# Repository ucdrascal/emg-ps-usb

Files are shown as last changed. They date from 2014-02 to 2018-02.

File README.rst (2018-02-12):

==========
emg-ps-usb
==========

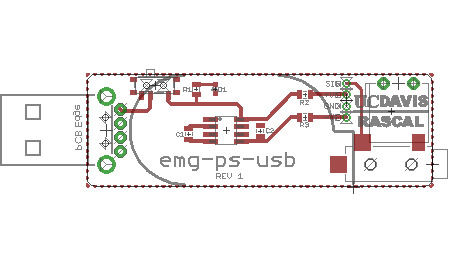
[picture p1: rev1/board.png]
Board screenshot


Description
===========
This is a power supply design for powering Motion Lab Systems Y03 or Z03 EMG
preamplifiers with a standard USB port. The board is designed to function like
a USB dongle with EMG electrode leads coming from it and a 1/8" `TS phone
connector`_ output (e.g. to connect to a computer's microphone port).

It uses a charge pump voltage converter chip to generate -5V from +5V USB
power. It is recommended that the design in the current state be used only with
USB ports belonging to devices isolated from mains earth (ground). This is
because there is no galvanic isolation between the USB port's ground and the
ground electrode, which connects directly to the user. It was originally
designed to connect to Android tablets which have a full-size USB A jack and
a TRRS headset inputs.

Parts
=====
Integrated circuits:

* `Analog Devices ADM660`_ switched-capacitor voltage converter

Electromechanical:

* Apem MA12R/TR SPDT switch
* CUI MJ-3523-SMT 3.5mmm mono phono jack
* Molex 480390001 USB-A connector
* TE Connectivity 284093-2 2x1 screw terminal block
* MyCableMart.com 6" 3.5mm mono male to male cable

Discrete components:

* Samsung CL21A106KAYNNNE 10uF ceramic capcaitor
* Panasonic ERJ-6GEYJ101V 100 Ohm thick film resistor
* Panasonic ERJ-6GEYJ102V 1k Ohm thick film resistor
* OSRAM LS L29K-G1J2-1-Z red LED

Details, including vendor links and prices are in bill-of-materials.ods.

License
=======

The contents of this repository are licensed under the `CC-BY 4.0 license`_.

.. REFERENCES
.. _`Analog Devices ADM660`: http://www.analog.com/en/power-management/switched-capacitor-converters/adm660/products/product.html
.. _`TS phone connector`: https://en.wikipedia.org/wiki/Phone_connector_(audio)
.. _`CC-BY 4.0 license`: https://creativecommons.org/licenses/by/4.0/

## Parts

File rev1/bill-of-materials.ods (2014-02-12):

Manufacturer | Part Number | Description | Qty | Unit Price | Vendor Part Number | Vendor Link
Analog Devices | ADM660ARZ | Charge pump converter | 1 | 4.59 | ADM660ARZ-ND | http://www.digikey.com/product-detail/en/ADM660ARZ/ADM660ARZ-ND/820185
Molex Inc. | 480390001 | USB-A connector | 1 | 1.19 | WM17117-ND | http://www.digikey.com/product-detail/en/0480370001/WM17117-ND/857603
Apem Inc. | MA12R/TR | SPDT switch | 1 | 1.10 | 679-1847-1-ND | http://www.digikey.com/product-detail/en/MA12RTR/679-1847-1-ND/1973774
TE Connectivity | 284093-2 | 2x1 screw terminal block | 1 | 1.11 | A98369-ND | http://www.digikey.com/product-detail/en/284093-2/A98369-ND/1136747
CUI Inc. | MJ-3523-SMT | 3.5mm mono phone jack | 1 | 1.34 | CP-3523MJCT-ND | http://www.digikey.com/product-detail/en/MJ-3523-SMT/CP-3523MJCT-ND/669691
OSRAM Opto Semiconductors Inc | LS L29K-G1J2-1-Z | red LED | 1 | 0.17 | 475-2506-1-ND | http://www.digikey.com/product-detail/en/LS%20L29K-G1J2-1-Z/475-2506-1-ND/1802633
Panasonic Electronic Components | ERJ-6GEYJ102V | 1k Ohm resistor | 1 | 0.10 | P1.0KACT-ND | http://www.digikey.com/product-detail/en/ERJ-6GEYJ102V/P1.0KACT-ND/42833
Panasonic Electronic Components | ERJ-6GEYJ101V | 100 Ohm resistor | 2 | 0.10 | P100ACT-ND | http://www.digikey.com/product-detail/en/ERJ-6GEYJ101V/P100ACT-ND/21875
Samsung Electro-Mechanics America, Inc | CL21A106KAYNNNE | 10uF ceramic capacitor | 2 | 0.25 | 1276-2891-1-ND | http://www.digikey.com/product-detail/en/CL21A106KAYNNNE/1276-2891-1-ND/3890977
MyCableMart.com | FS-MONO-06IN-MM | 3.5mm mono male to male cable | 1 | 0.81 | FS-MONO-06IN-MM | http://www.mycablemart.com/store/cart.php?m=product_detail&p=4270
 |  |  | Subtotal | 11.11
 |  |  | Printing | 2.87
 |  |  | Total | 13.96

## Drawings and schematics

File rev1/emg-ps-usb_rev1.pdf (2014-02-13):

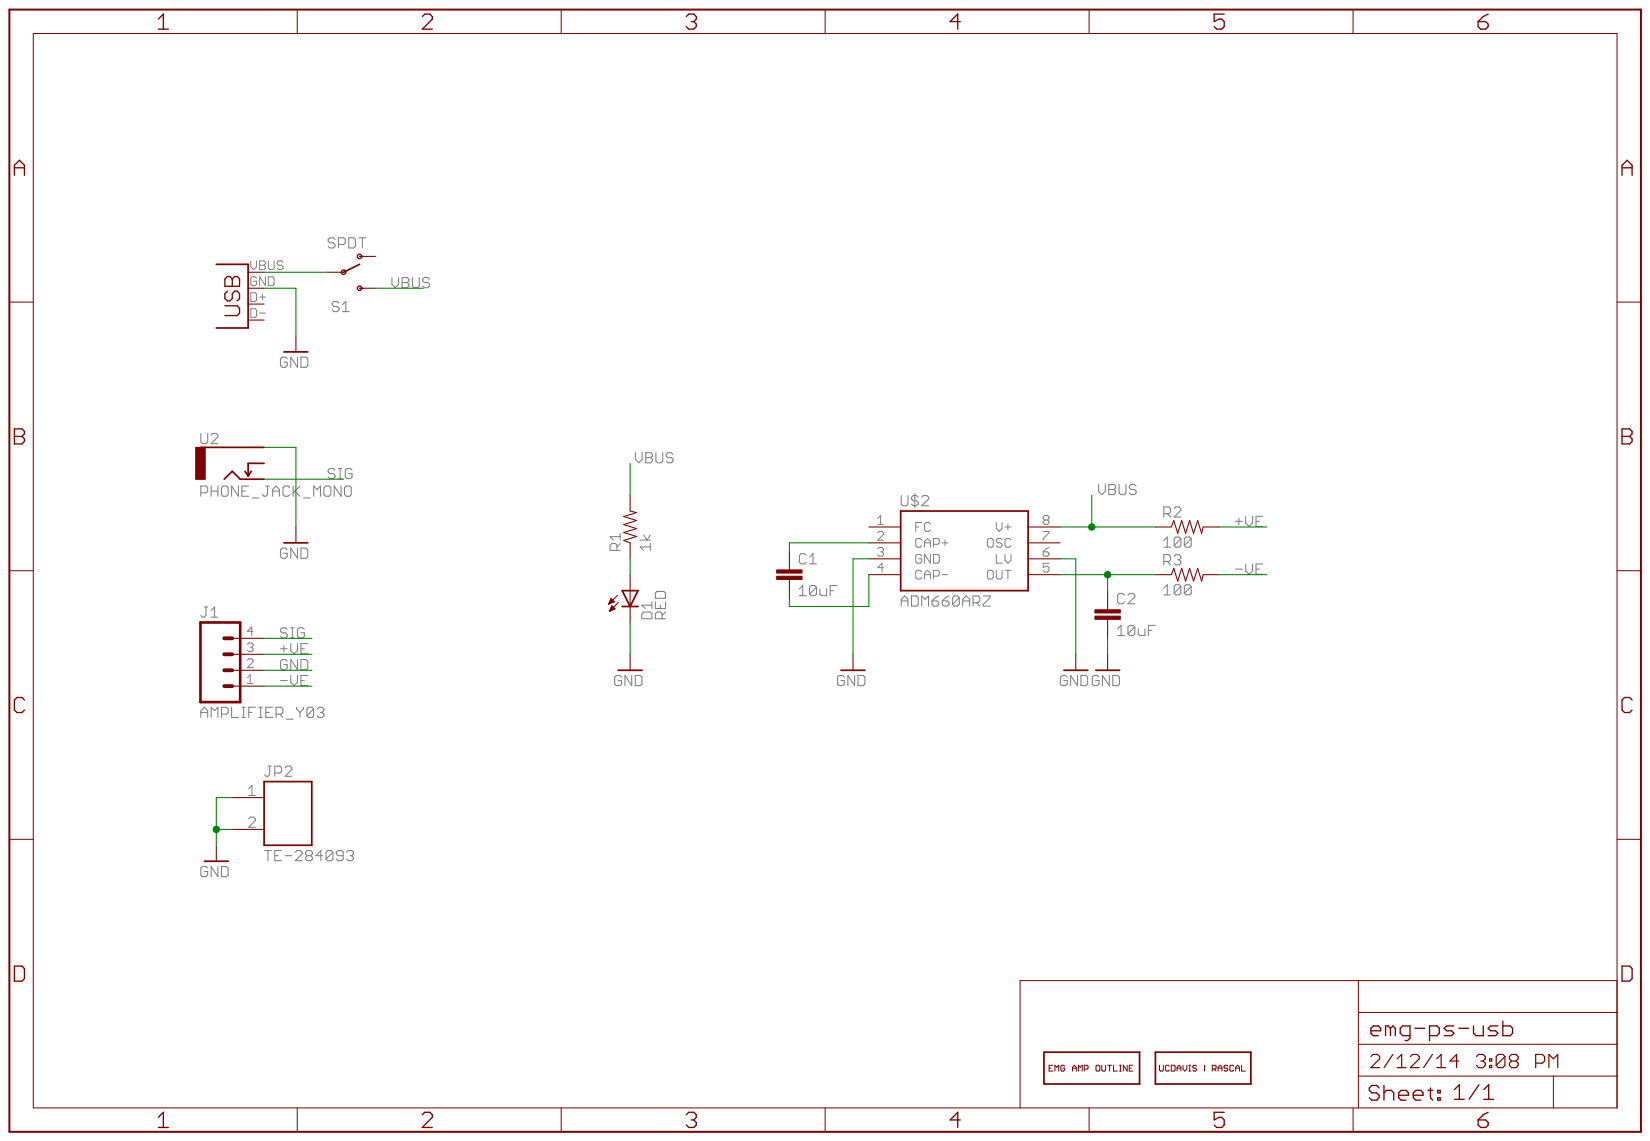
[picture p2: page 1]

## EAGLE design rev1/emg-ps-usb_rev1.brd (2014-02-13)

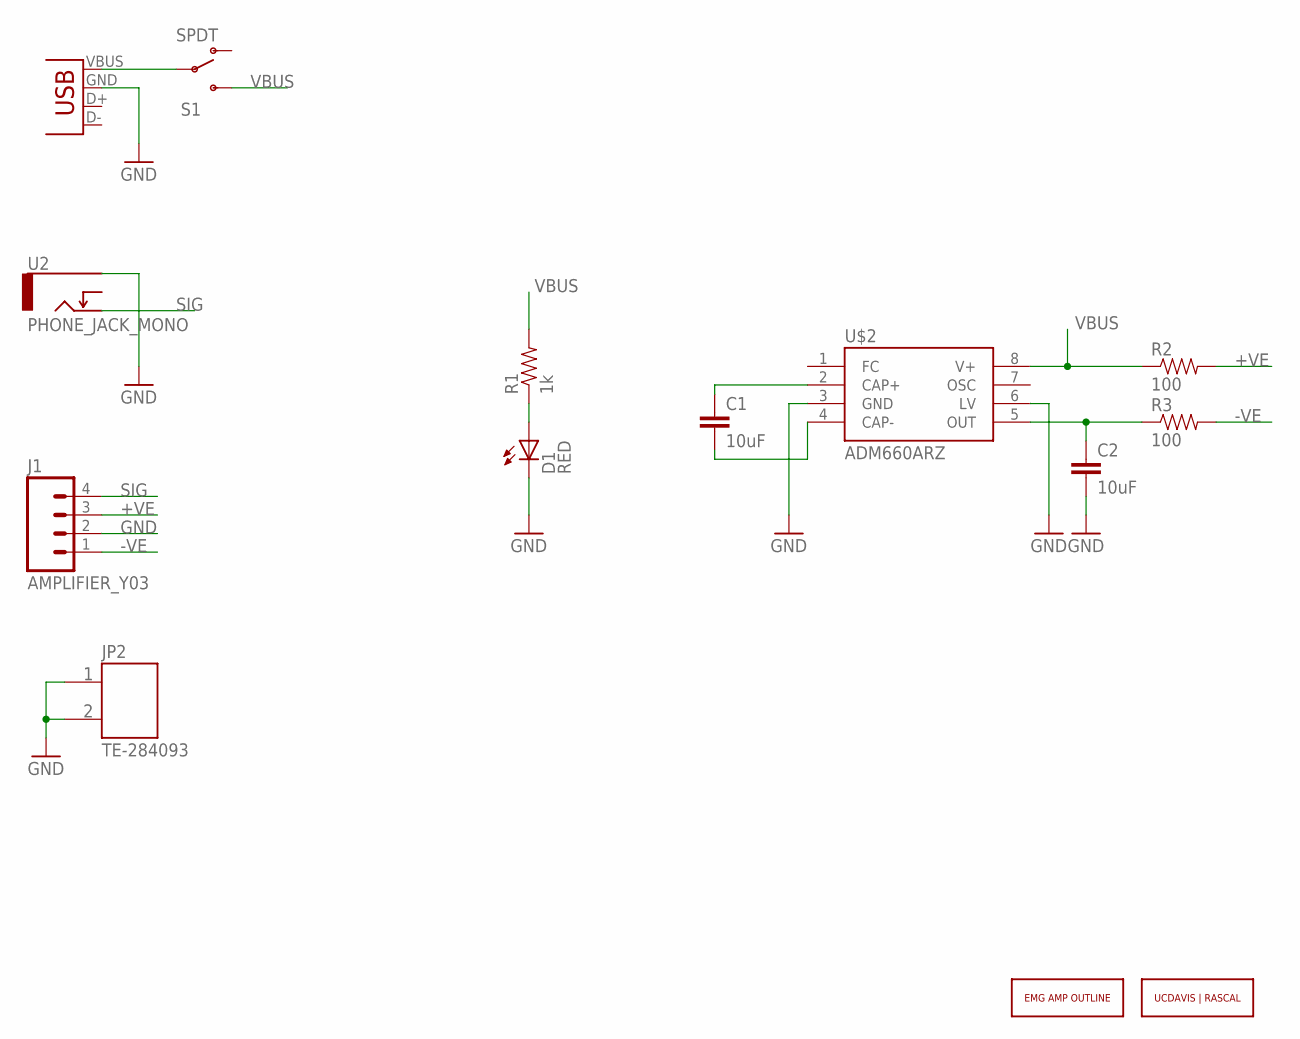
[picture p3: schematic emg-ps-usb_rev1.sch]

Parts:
C1, C2: 10uF; 0805
D1: RED; LED-0603
J1: AMPLIFIER_Y03; AMPLIFIER_WTB
JP1: USB-A-H
JP2: TE-284093
R1: 1k; 0805
R2, R3: 100; 0805
S1: SPDT; SWITCH-SPST-SMD-A
U2: PHONE_JACK_MONO; MJ-3523-SMT
U$1: UCDAVIS-RASCAL_LOGO-2LINE; UCDAVIS-RASCAL_LOGO
U$2: ADM660ARZ; SOIC8
U$3: EMG_AMP_OUTLINE-Y03ENDS; EMG_Y03_OUTLINEENDS

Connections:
+VE: J1.3, R2.2
-VE: J1.1, R3.2
GND: C2.2, D1.C, J1.2, JP1.GND (VBUS), JP2.P$1 (1), JP2.P$2 (2), U2.P$1, U$2.3 (GND), U$2.6 (LV)
unnamed: JP1.VBUS (GND), S1.2
unnamed: D1.A, R1.1
unnamed: C2.1, R3.1, U$2.5 (OUT)
unnamed: C1.2, U$2.4 (CAP-)
unnamed: C1.1, U$2.2 (CAP+)
SIG: J1.4, U2.P$2
VBUS: R1.2, R2.1, S1.3 (S), U$2.8 (V+)

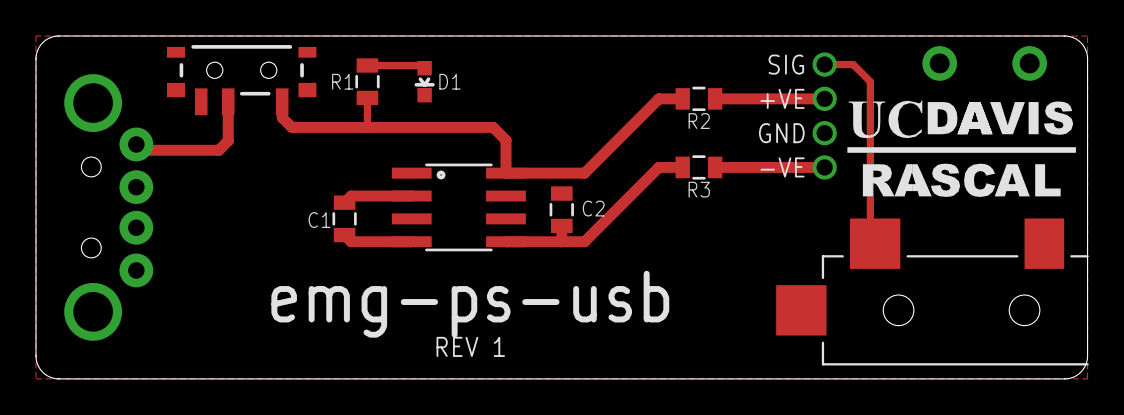
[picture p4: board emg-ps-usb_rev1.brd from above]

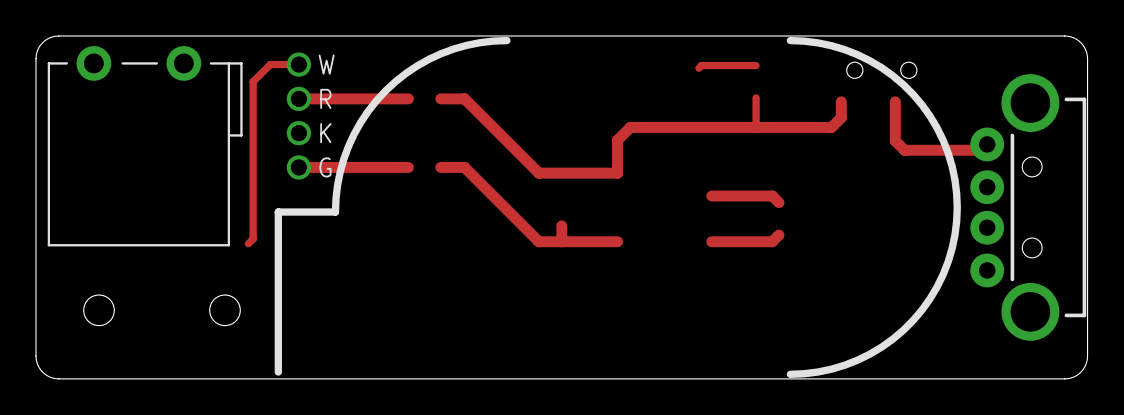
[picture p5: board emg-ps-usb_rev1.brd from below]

Board: 2 copper layers, 58.4 x 19.1 mm, 14 parts (3 on the bottom side), 10 nets.

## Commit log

2013-09-29 Initial commit. Board is essentially done but needs thorough review.
    [bill-of-materials.ods, emg-ps-usb.brd, emg-ps-usb.sch]
2013-09-29 Cleaned up schematic and added a frame.
    [emg-ps-usb.brd, emg-ps-usb.sch]
2013-09-29 Added labels to the EMG amp connector. Decreased size of component names.
    [emg-ps-usb.brd]
2013-09-29 Now using EMG amp outline and UCDAVIS|RASCAL logo from ucdrascal-eagle-lib.
    [emg-ps-usb.brd, emg-ps-usb.sch]
2013-09-29 Refreshed library parts (UCDAVIS|RASCAL logo).
    [emg-ps-usb.brd, emg-ps-usb.sch]
2013-09-30 Shifted some component labels to get them out of tStop.
    [emg-ps-usb.brd]
2014-01-13 Cleaned up layout and routing. Moved LED to top and removed UCDRASCAL logo.
    [emg-ps-usb.brd, emg-ps-usb.sch]
2014-02-12 Added UCDRASCAL logo. Swapped the 4x1 Molex connector for just a wire to board interface. Updated BOM.
    [bill-of-materials.ods, emg-ps-usb.brd, emg-ps-usb.sch]
2014-02-13 Added pad labels on amplifier side. Ordered the board and copied to rev1 subfolder.
    [bill-of-materials.ods, emg-ps-usb_rev1.brd, emg-ps-usb_rev1.sch]
2018-02-12 Added screenshot of board to README.

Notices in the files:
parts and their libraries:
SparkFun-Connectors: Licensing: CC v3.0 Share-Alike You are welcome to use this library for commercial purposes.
